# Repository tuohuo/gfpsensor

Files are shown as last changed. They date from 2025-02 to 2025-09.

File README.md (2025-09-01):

# Advancing Recombinant Antibody Production in E. coli: Optimization of Expression and Purification via Dual GFP Promoter and Imaging Technology
### Anttoni Korkiakoski, Sami Oksanen, Tuomas Huovinen

Additional information for the assembly of GFP biosensor described in Korkiakoski et al. (2025) Advancing Recombinant Antibody Production in E. coli: Optimization of Expression and Purification via Dual GFP Promoter and Imaging Technology.

# Abstract
Fed-batch fermentation results in high recombinant protein titers in limited culture volumes. Therefore, it is the preferred operation mode in the bioprocess industry. Optimizing feeding, induction, and harvest timing is a significant time-consuming challenge in bioprocessing complicated by the fact that expressed target protein is rarely detectable in real-time. In this study, the construction of an online sensor is described integrating a dual GFP promoter construct, a blue LED and a Raspberry Pi camera for real-time monitoring of recombinant antibody expression in Escherichia coli. The dual promoter construct allows simultaneous expression of GFP in the cytoplasm and the recombinant antibody in the periplasm, enabling the use of GFP fluorescence as a proxy for protein yield. GFP fluorescence correlated with Fab and nanobody expression over time and the relative quantity of fluorescence predicted the extent of induction. In nanobody fed-batch fermentations, the decreasing rate of dGFP/dt was a valuable parameter for identifying the optimal harvest point, minimizing excessive incubation time and reducing nanobody leakage into the medium. It was further demonstrated that quantitation of pixel values from RGB images captured with a Raspberry Pi 8  MP camera in the flow cell resulted in equal sensitivity for GFP detection as that achieved with a μPMT and photodiode sensors. The 3D-printable GFP sensor station is a valuable tool for process optimization and for educating bioprocess engineering students through real-time visualization of promoter activation.

# Python script for running the sensor:

````python
# Libraries
from picamera import PiCamera
import time
from fractions import Fraction
import datetime
import RPi.GPIO as GPIO
from PIL import Image
import numpy as np
import matplotlib.pyplot as plt
import pandas as pd

# Camera setup
camera = PiCamera(framerate=Fraction(1,6))
camera.resolution = (1600, 1200)
camera.shutter_speed = 1000000    # max 6M µs for Cam V2.1 
camera.iso = 800                         # max: ISO800 
camera.exposure_mode = 'off'          # does not make automatic gain adjustments

ledpin = 18             
GPIO.setmode(GPIO.BOARD)       # use PHYSICAL GPIO Numbering
GPIO.setup(ledpin, GPIO.OUT)     # set RGBLED pins to OUTPUT mode

#Image processing
ts = []
gys = []
bys = []
rys = []
xs = []
names = [] #added 220916TH

plt.ion()
figure, ax = plt.subplots(figsize=(8,6))
plt.xlabel("Time (h)",fontsize=18)
plt.ylabel("GFP fluorescence (pixel sum)",fontsize=18)
plt.title("Dynamic Plotting",fontsize=25)

i=1
time_1 = time.time()
print("here we are")
try:
    while True:
        GPIO.output(ledpin, GPIO.HIGH) #BLUE LED ON TO MEASURE GFP GREEN 
        time.sleep(2)
        #COMMON TIME
        now = datetime.datetime.now()
        timestamp = now.strftime("%B_%d_%H%M")
        time_2 = time.time()
        time_d = float((time_2 - time_1)/3600)
        hours = "{:.2f}".format(time_d)

        #PROCESS RED, GREEN AND BLUE
        filename = "img_" + str(i) + "_" + timestamp + "_Green" + '.jpg'
        camera.capture(filename)
        print(filename)
        img = Image.open(filename).convert('RGB')
        img.load()
        sequence_of_Gpixels = np.asarray(img.getchannel(1), dtype="int32")
        sequence_of_Bpixels = np.asarray(img.getchannel(2), dtype="int32")
        sequence_of_Rpixels = np.asarray(img.getchannel(0), dtype="int32")
        sumgreen = sequence_of_Gpixels.sum()
        sumblue = sequence_of_Bpixels.sum()
        sumred = sequence_of_Rpixels.sum()
        time.sleep(2)
        GPIO.output(ledpin, GPIO.LOW) #BLUE LED OFF
            
         #ADD PIXEL VALUES TO LIST
        ts.append(timestamp)
        gys.append(sumgreen)
        bys.append(sumblue)
        rys.append(sumred)
        xs.append(time_d)
                
        df = pd.DataFrame({"Time" : xs, "SumG" : gys, "SumB" : bys, 
                           "SumR" : rys, "Stamp" : ts}).sort_values(by = "Time")
        line1, = ax.plot(df.Time, df.SumG, "g-")
        line1.set_xdata(df.Time)
        line1.set_ydata(df.SumG)
        line2, = ax.plot(df.Time, df.SumB, "b-")
        line2.set_xdata(df.Time)
        line2.set_ydata(df.SumB)
        line3, = ax.plot(df.Time, df.SumR, "r-")
        line3.set_xdata(df.Time)
        line3.set_ydata(df.SumR)
                      
        figure.canvas.draw()
        figure.canvas.flush_events()    
        print(df)
        time.sleep(296)
        i+=1
     
except KeyboardInterrupt: #Press Ctrl+C to interrupt
    timestamp2 = now.strftime("%Y_%B_%d_%H%M")
    df.to_csv('output_' + timestamp2 + '.csv')
    camera.close()
    GPIO.cleanup()
    pass
````

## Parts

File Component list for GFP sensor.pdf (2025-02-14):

Component list

Sensor case and tubing
Item | Description | Qty
Flow cell holder | 3D printable part | 1
Hinge | 3D printable part | 2
Sensor box | 3D printable part | 1
Sensor lid | 3D printable part | 1
Pasteur pipette | 107 mm; o.d. 0.7 mm; Dremel cut and polished (John Poulten) 1
Novosil silicone tubing | 1.6 m; with i.d./o.d.: 3/6 mm (Fisher scientific) | 2
PharMed BPT tubing | 100 mm; with i.d./o.d.: 3.2/6.3 mm (Saint-Gobain) | 1
Male luer lock connectors | with lock ring for 3.2 mm i.d. tubing, nylon (MasterFlex) | 2
Female luer lock connectors | with lock ring for 3.2 mm i.d. tubing, nylon, (MasterFlex) | 2
Pan head screw | M4x 40 mm (locking hinges in place) | 4
Pan head screw | M4x 16 mm (in hinge to calibrate the angle btn. modules) | 2
Hexagon thin nut | M4 (& washers) | 20
Cheese head screw | M4x 80 mm (fastening screws for modules in hinges) | 2

LED module
Item | Description | Qty
LED module part1 | 3D printable part | 1
LED module part2 | 3D printable part | 1
LED module part3 | 3D printable part | 1
LED module part4 | 3D printable part | 1
Excitation light filter | o.d.: 1 inch; FB470-10 (Thorlabs) | 1
Pan head screw | M4x 16 mm | 4
Countersunk flat head screw | M4x 16 mm | 2
Blue LED | 5 mm; 12 V with resistor #LED 5SUK12V (Elgood Oy) | 1
metal holder for LED w lens | focal length 15 mm #SML1083, Signal Construct)1
lens | #SML1083 (Signal Construct), lens only | 1
tinned copper wire/jumpers | ~ 250 mm; 30AWG; core diam. 0.25mm; o.d. 0.6mm | 4
Proto-board PCB | Piece of 20x 15 mm | 1
Female header strip | 2 sockets cut for soldering on PCB; Rpi pin connection | 1
Transistor | NPN bipolar #S8050 | 1
Resistor | 1 kOhm | 1

Camera module
Item | Description | Qty
Camera module part1 | 3D printable part | 1
Camera module part2 | 3D printable part | 1
Camera module part3 | 3D printable part | 1
Camera module part4 | 3D printable part | 1
Pan head screw | M4x 30 mm | 2
Pan head screw | M4x 12 mm (holding camera cable slot lid in place) | 1
Countersunk flat head screw | M4x 16 mm | 2
Camera | Raspberry Pi 8 MP (Raspberry Pi) | 1
Camera cable | 300 mm, 15 pin Flex Cable for Raspberry Pi camera | 1
lens | #SML1083 (Signal Construct), lens only | 1
Emission light filter | o.d.: 1 inch; (FB510-10, Thorlabs). | 1

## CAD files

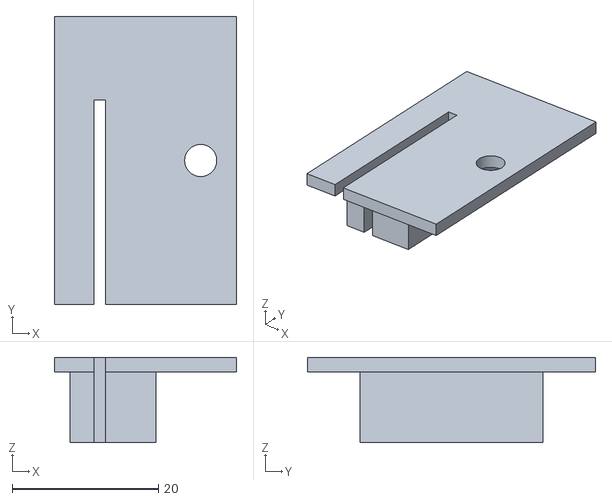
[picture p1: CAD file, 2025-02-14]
Camera module/Camera_module_part3.stl
24.9 x 39.4 x 11.6

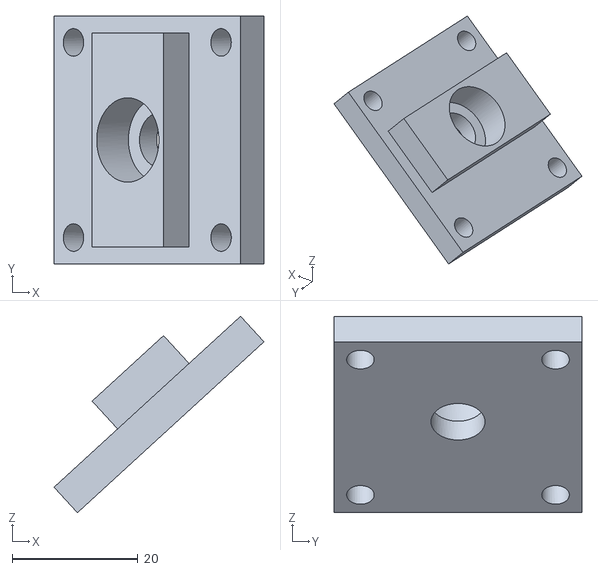
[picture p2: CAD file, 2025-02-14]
LED module/Led_module_part2.stl
33.4 x 39.4 x 31.2

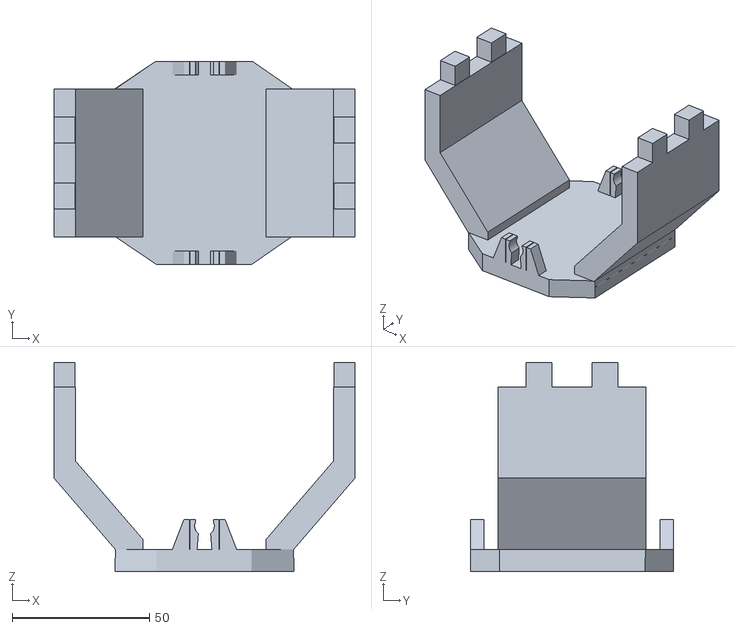
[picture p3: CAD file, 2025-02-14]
Sensor box/Flow cell holder.stl
109.6 x 74.0 x 76.2

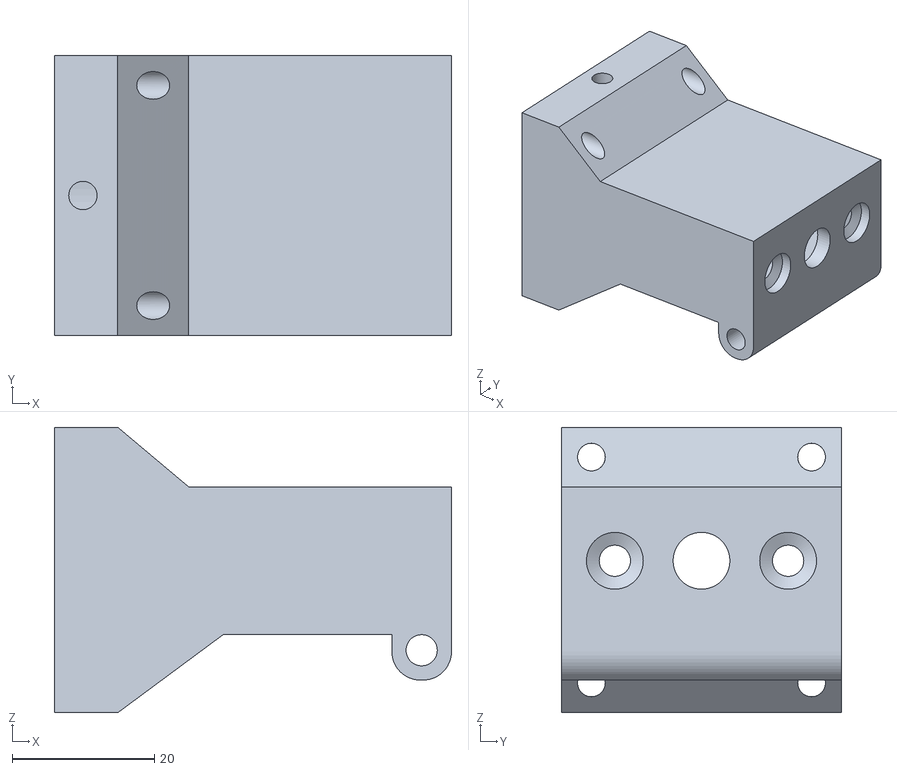
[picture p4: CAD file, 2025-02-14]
Camera module/Camera_module_part1.stl
55.9 x 39.4 x 40.2

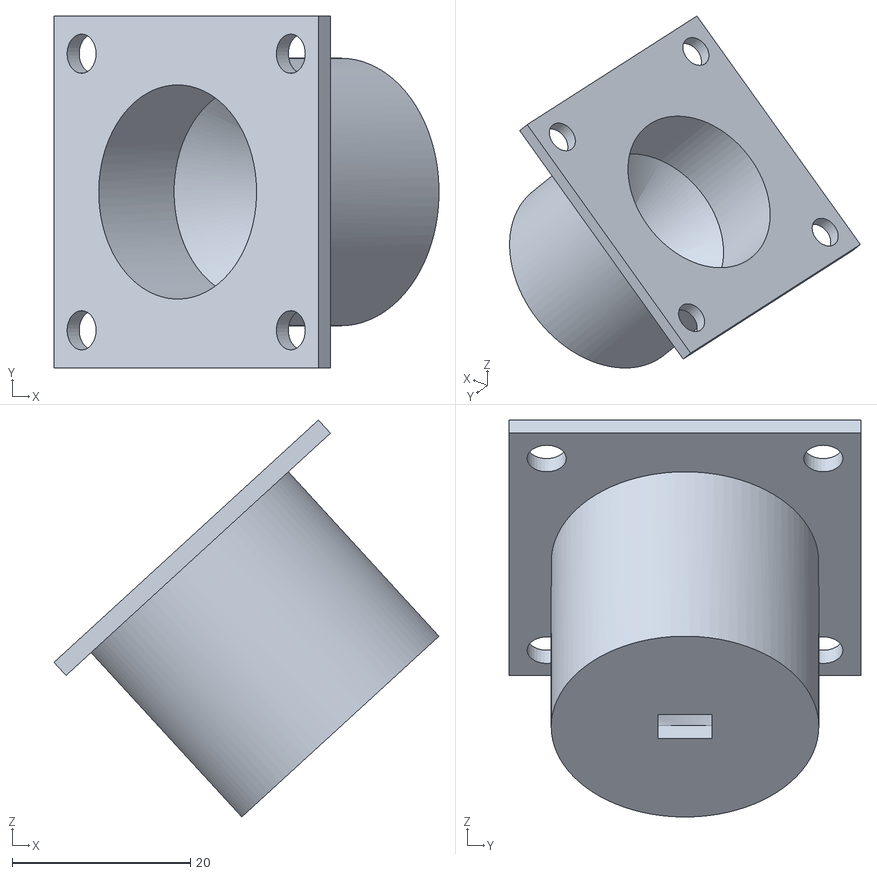
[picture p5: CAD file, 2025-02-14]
LED module/Led_module_part4.stl
43.2 x 39.4 x 44.5

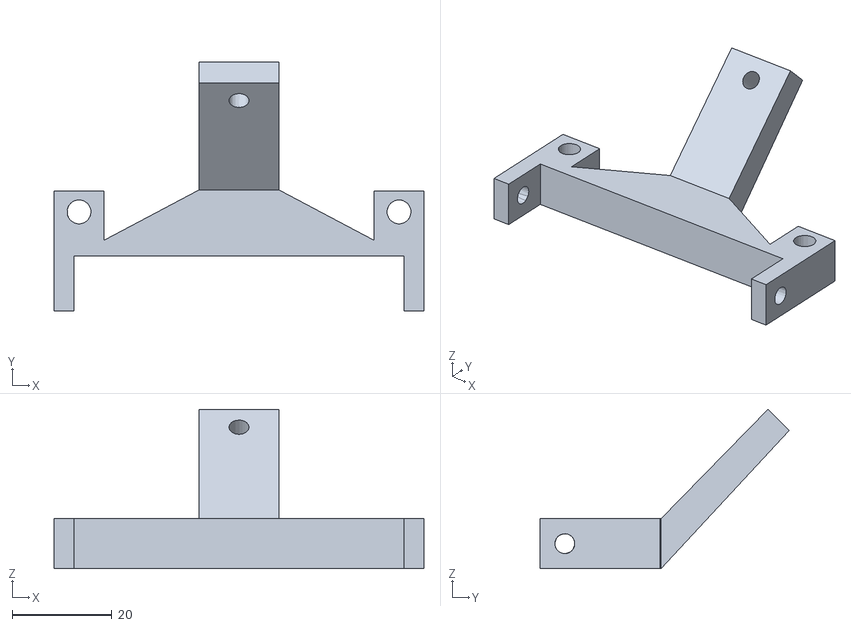
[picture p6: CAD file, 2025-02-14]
Sensor box/Hinge.stl
74.0 x 49.9 x 31.9

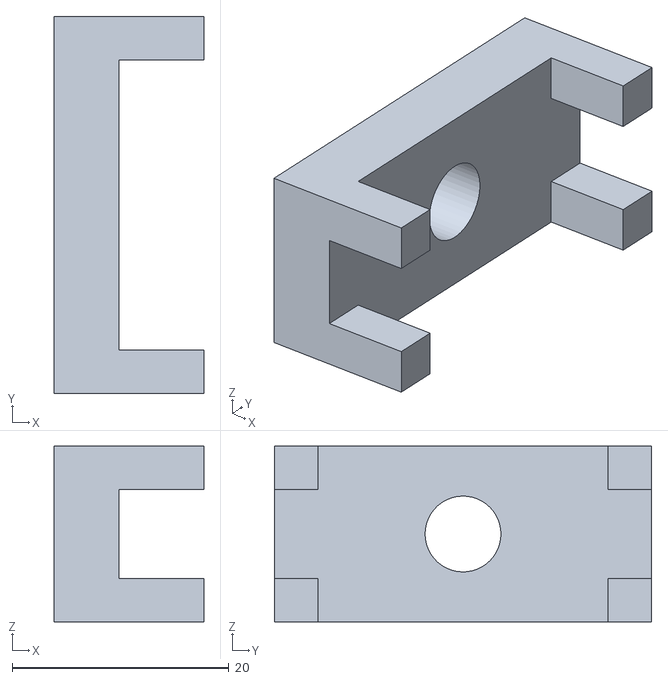
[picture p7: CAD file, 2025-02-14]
Camera module/Camera_module_part2.stl
13.8 x 34.8 x 16.2

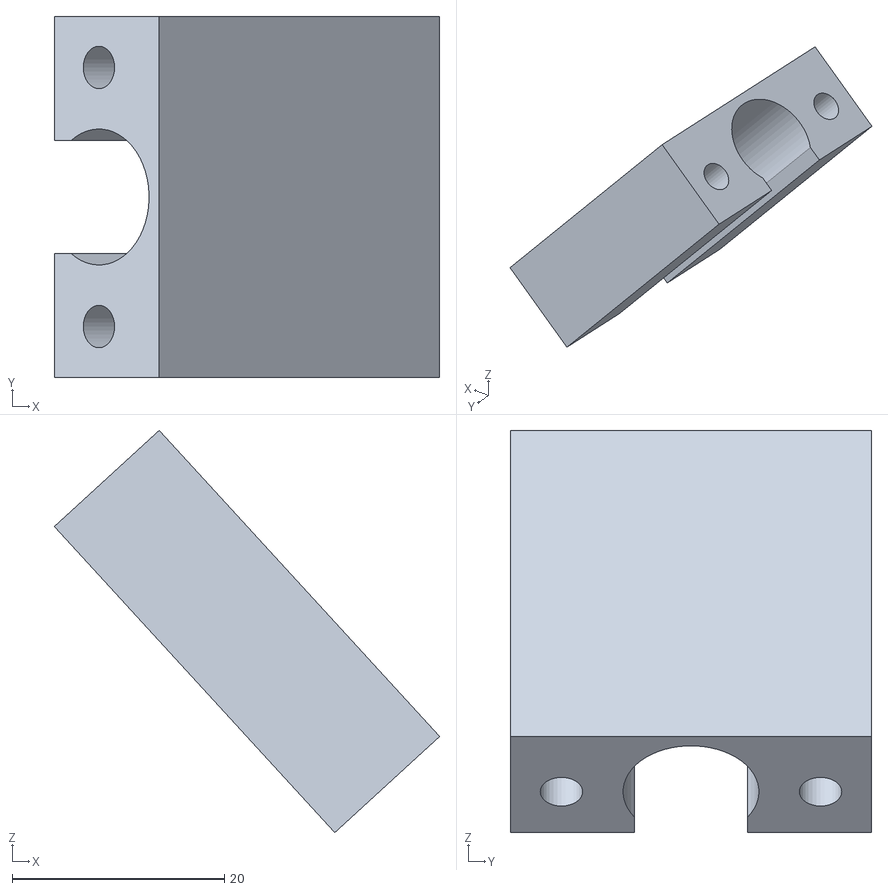
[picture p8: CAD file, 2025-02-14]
LED module/Led_module_part3.stl
36.3 x 34.0 x 37.9

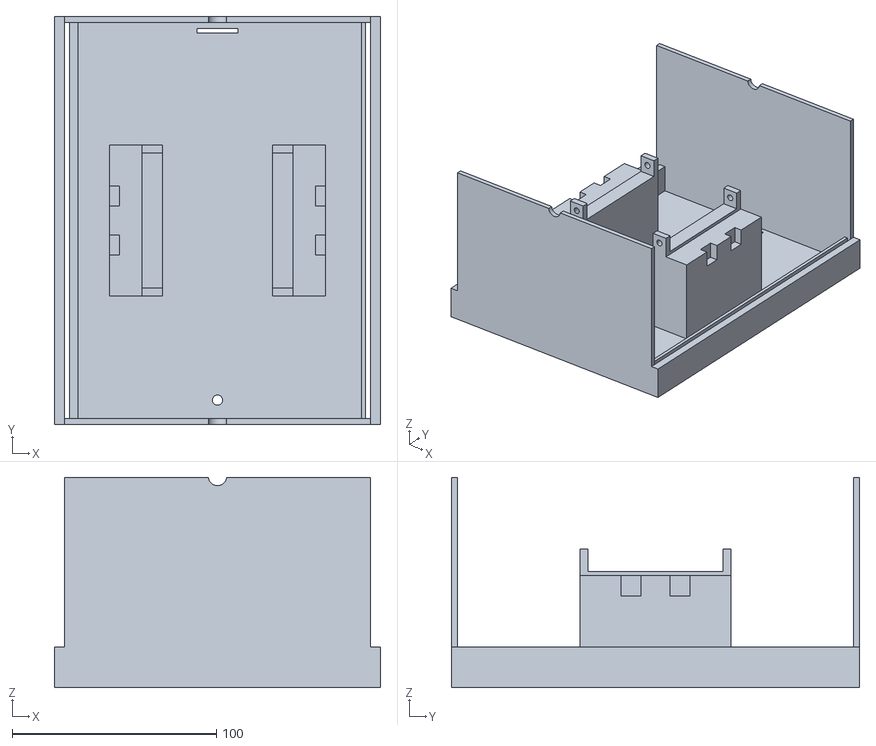
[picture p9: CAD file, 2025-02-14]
Sensor box/Sensor box.stl
160.0 x 200.0 x 103.0

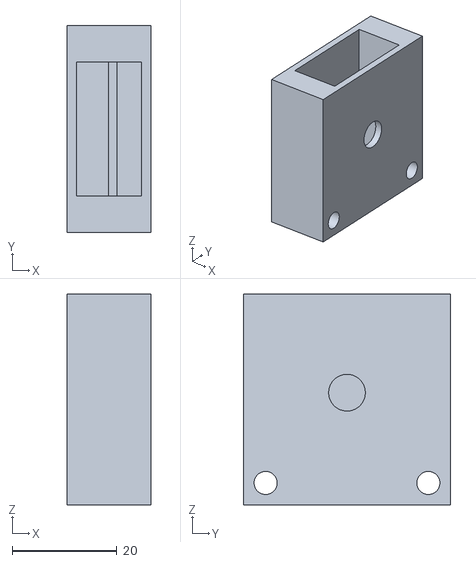
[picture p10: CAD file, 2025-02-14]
Camera module/Camera_module_part4.stl
16.0 x 39.4 x 40.2

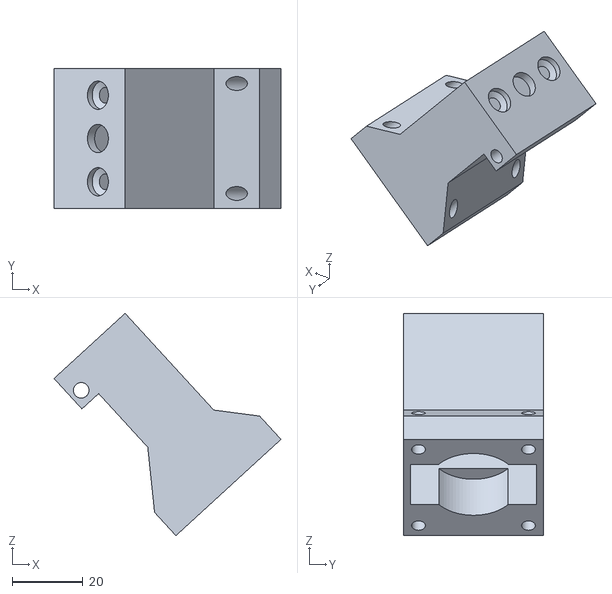
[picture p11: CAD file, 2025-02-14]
LED module/Led_module_part1.stl
64.0 x 39.4 x 62.7

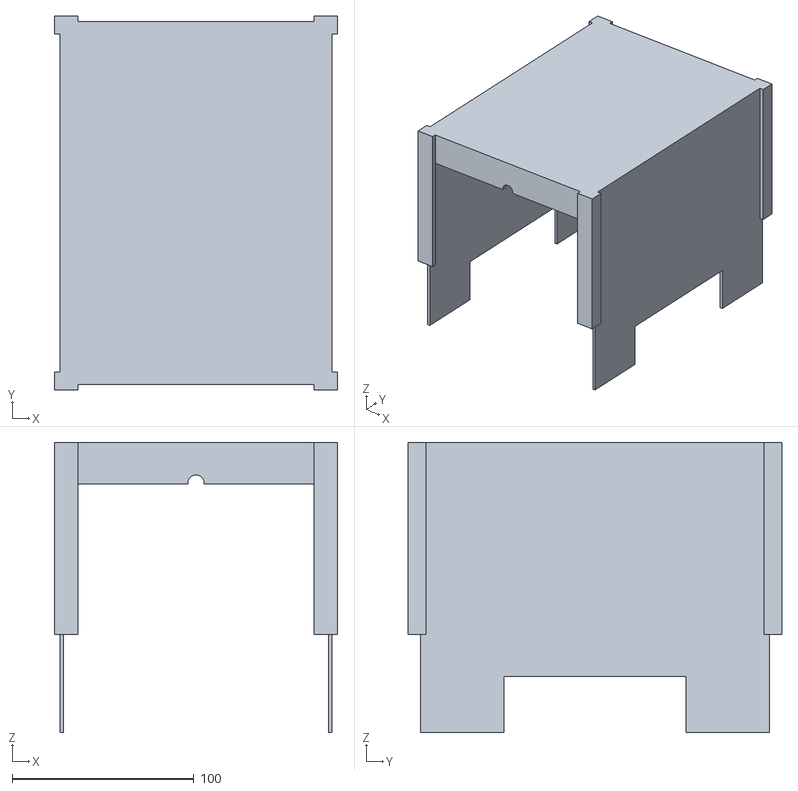
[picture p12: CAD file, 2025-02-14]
Sensor box/Sensor lid.stl
156.0 x 206.0 x 160.0
